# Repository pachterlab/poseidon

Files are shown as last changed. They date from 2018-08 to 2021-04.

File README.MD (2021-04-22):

poseidon_logo



## poseidon: Open source bioinstrumentation
An easy-to-use, highly customizable, and open source syringe pump and microscope system.

**Documentation**: https://pachterlab.github.io/poseidon/

**Paper**: A. Sina Booeshaghi, Eduardo da Veiga Beltrame, Dylan Bannon, Jase Gehring and Lior Pachter, <a href="https://www.nature.com/articles/s41598-019-48815-9">Principles of open source bioinstrumentation applied to the poseidon syringe pump system</a>, Scientific Reports <b>9</b>, Article number: 12385 (2019).

## The tl;dr

The poseidon syringe pump and microscope system is an open source alternative to commercial systems. It costs less than \$400 and can be assembled in an hour. It uses 3D printed parts and common components that can be easily purchased either from Amazon or other retailers. The microscope and pumps can be used together in microfluidics experiments, or independently for other applications. The pumps and microscope can be run from a Windows, Mac, Linux, or Raspberry Pi computer with an easy to use GUI.

ortho_edit

## What is included?
* Computer Aided Design (CAD) files of the 3D printed components.
* Controller software (Python) and a graphical user interface (GUI) to control the pumps.
* Arduino firmware to send commands to the motors and receive commands from the GUI.
* Bill of materials for sourcing and purchasing materials.
* Detailed assembly instructions of hardware components.
* Single click executable files for Mac, Windows, Linux, and Raspberry Pi systems.

<p align="center">
  
</p>

## Getting Started
### 3D printing components and purchasing hardware
The 3D printed components can be fabricated on any desktop fused filament fabrication (FFF) 3D printer. They were designed using [Autodesk Fusion 360](http://autodesk.com/fusion360), a proprietary CAD software that offers free academic licenses.

- Fusion360 interactive view of [poseidon microscope CAD](http://a360.co/2krZoEk).
- Fusion360 interactive view of [poseidon pump](https://a360.co/2Ph19kC).
- STL, STEP, IGES, Fusion 360 archive files, and bill of materials are available in the `HARDWARE/` folder.
- Bill of materials with prices and vendor links on a [Google Spreadsheet](https://docs.google.com/spreadsheets/d/1AHBLf0PbtGDgqNbbK6QO31s7ES9_1uCw_NeKWHHPTM4/edit?usp=sharing).

### Build Videos
Syringe Pump: https://www.youtube.com/watch?v=7YSiO6usR1M  
Microscope  : https://www.youtube.com/watch?v=Szg-vjukonA  
Arduino     : https://www.youtube.com/watch?v=Xl02fsRCJ7U  
Raspberry Pi: https://www.youtube.com/watch?v=g3pXNY8snOg  

Running poseidon: https://youtu.be/VmoB_fPc4L4

### Setting up the Arduino 
We use the [Arduino CNC shield](http://wiki.keyestudio.com/index.php/Ks0095_Arduino_CNC_Kit_/_CNC_Shield_V3.0_%2Bkeyestudio_Uno_R3%2B4pcs_a4988_Driver_/_GRBL_Compatible)
to allow for up to three pumps can be controlled from a computer or from the Rapsberry Pi microscope.

The software is configured to run the stepper motors with 200 steps per revolution at 1/32 microstepping, which translates to 6400 steps per rotation. To configure this, it is necessary to add 3 jumpers between the M0, M1 and M2 pins of the Arduino CNC shield. More information about microstepping can be found in the product page for the [DRV8825 Stepper Motor Driver](https://www.pololu.com/product/2133), which is used by the CNC shield. See the build videos for more detail. 

The Arduino should be flashed with the `arduino_serialCOM_v0.1.ino` sketch, available in the `SOFTWARE/` folder.

**Make sure to download and install the [AccelStepper library](https://www.airspayce.com/mikem/arduino/AccelStepper/index.html)**. To install, unzip the zip file to the libraries sub-folder of your sketchbook, if you get stuck here is a [how-to](https://www.arduino.cc/en/guide/libraries).

The pumps are driven by an Arduino board that interprets commands sent via USB and sends the signals to control the stepper motor movement. For directions on how to flash an arduino please refer to the official guide: https://www.arduino.cc/en/Guide/HomePage

### Installing software
The Python scripts are available in the `SOFTWARE/` folder. The GUI was created using [Qt designer](http://doc.qt.io/qt-5/qtdesigner-manual.html), a drag and drop application for organizing buttons that allows the used to easily make modifications. This GUI is used to interface with a Python script that controls both the microscope and Arduino via USB. 

The software you will need to run on your computer in order to control the Arduino is the `poseidon_main.py` script located in the `SOFTWARE/` folder (also included is `poseidon_controller_gui.py` which is needed). 

You have the option of either (1) running from the source code in Python or (2) choosing the appropriate binary file below for your operating system and executing it. Before you run the controller code, MAKE SURE YOU HAVE INSTALLED THE ARDUINO FIRMWARE!!

## Startup Checklist
Before starting the Python controller, make sure
1. The Arduino has the firmware uploaded to it
2. The Arduino is connected via USB to the computer or Rapsberry Pi microscope
3. You have appropriately placed jumpers on the CNC Sheild to allow for microstepping and hardware enabling (discussed in build video).
4. The CNC shield is powered, and that all motors are plugged in to the CNC sheild

## Running the software and Testing the pumps
There are two ways to run the controller. The easiest way is to just double click the executable available below. Simply download the executable, double click it, and begin using it. Navigate to the **Releases** tab at the top to find the following executables.

- Windows
- Mac OS
- Ubuntu (coming soon)
- Raspbian

# Tips/Hints
Things that we have learned along the way that may help with your build.
- Basic tests indicate that pressures up to 4 MPa can be acheived with 1 microstep and a 1 mL syringe.

- Set the current limit on your motor controller to vary the stall torque. Increasing the current to the motor increases the stall torque and increases the max pressure that your syringe pump can run at. [How to set the current limit](https://www.youtube.com/watch?feature=player_embedded&v=89BHS9hfSUk).

- We recommend [changing the password on the Raspberry Pi](https://raspberrypi.stackexchange.com/questions/67181/how-to-change-a-password) for added security.

- The speeds and flow rates of the system are limited by the microstepping and the syringe size used.

flow_rates

---------------------------------------------------

If you want to run the system from the source code then follow the instructions below.
### Windows, Mac, Linux
First make sure you have Python 3 installed on your machine. Then install PyQt5. To install PyQt5 use `brew install pyqt5` or `conda install pyqt` if you are using anaconda. If you are on Linux you can do `sudo apt-get install python3-pyqt5`. Now we need to add a few packages:
```
pip3 install --upgrade -pip
pip3 install pyserial
pip3 install opencv-python
```
On Linux opencv requires extra binaries
```
sudo apt-get install libatlas-base-dev
sudo apt-get install libjasper-dev
sudo apt-get install libqtgui4
sudo apt-get install libqt4-qt3support
sudo apt-get install libqt4-test
```
Now you can run 
```
# now the script can be called
python3.5 poseidon_main.py
```
### Raspberry Pi
To run `poseidon_main.py` on a Raspberry Pi with a fresh install of Raspbian, Python 3 with pyqt5 need to be installed, together with a few packages.
```
sudo apt-get install python3-pyqt5

# now need to use python3.5 gui.py to invoke the python3 that has pyqt5!
pip3 install --upgrade -pip
pip3 install pyserial
pip3 install opencv-python

# opencv requires a some extra binaries 
sudo apt-get install libatlas-base-dev
sudo apt-get install libjasper-dev
sudo apt-get install libqtgui4
sudo apt-get install libqt4-qt3support
sudo apt-get install libqt4-test

# now the script can be called
python3.5 poseidon_main.py
```
### Now that you have everything installed, go ahead and test it out!
(1) Select the port that your Arduino is plugged into. If you don't see the right port, press `update port`. 
(2) Set your microstepping
(3) Input appropriate settings
(4) Select `connect to controller`
(5) Select `Send all settings to controller`
(6) Go to the controller tab, select all three checkboxes and press `Jog +`

If the sleds are not moving in the right direction simply rotate the relevant stepper motor plug (that connects to the CNC shield) 180 degrees and plug it back in.

## How does it work, and how to modify it. (Very easy!)
The poseidon system was designed to be customizable. It uses the [Raspberry Pi](https://www.raspberrypi.org/)  and [Arduino](https://www.arduino.cc/) electronics boards, which are supported by a strong ecosystem of open source hardware and software, facilitating the implementation of new functionalities.

The pump driver uses an Arduino with a [CNC shield](https://blog.protoneer.co.nz/arduino-cnc-shield/) to run up to three pumps. Each pump has a stepper motor that drives lead screw which in turn moves a sled that is mounted on linear bearings. The displacement of the sled moves the syringe forward or backward allowing the user to dispel or intake liquid.

The controller station uses a Raspberry Pi with a touchscreen to connect to the Arduino and microscope via USB. Because the microscope and Arduino use USB connections, they can alternatively be connected to a computer instead of a Raspberry Pi. 

To modify the 3D models, users can either use Fusion 360 or any other CAD software. Simply open up the components, located in the `HARDWARE` folder, and get editing! Once you're done, go ahead and print out the parts and assemble them.

Most of the modifications to the code will be done in `poseidon_main.py` and to the GUI. If you want to edit the GUI, first make sure you have installed PyQt Designer (which should have been installed when you downloaded and installed PyQt5, so you can search for it on your computer `Designer.exe` (Windows) or `Designer` in your applications folder (Mac). Open up the `poseidon_controller_gui.ui` in Designer and make whatever modifications you'd like. Then when you are done, you need to convert the modified `.ui` file to a `.py` file. Go to the terminal, navigate to the folder where you have `poseidon_controller_gui.ui` and run the command `pyuic5 poseidon_controller_gui.ui > poseidon_controller_gui.py`.

When you are done editing the `poseidon_main.py` you can recreate the single click executable files by following the instructions below.

### Installing pyinstaller on Windows 7 and making a single executable for the Python controller
 
Using Python 3.7 (installing pyqt5 form pip) or 3.4 (installing pyqt5 from executable) on Windows 10 did not work. 
Python 3.7 yields terrible dependency errors from pyinstaller and with Python 3.4 after making the executable pyqt complains apparently because of windows 10. The solution was to use a machine with Windows 7. 

After installing Python 3.5.4 (https://www.python.org/downloads/release/python-354/), using the `Windows x86-64 executable installer`, these dependencies should install without problems:
```
python -m pip install pyqt5
python -m pip install pyserial
python -m pip install opencv-python
```
To compile a binary you should write `PyInstaller`, instead of `pyinstaller`...
```
python -m PyInstaller --version
python -m PyInstaller poseidon_main.py
```
Just doing `python -m PyInstaller gui.py` with Python 3.5 on windows 7 threw up some errors, the following line solved the issue.
Described here: https://stackoverflow.com/questions/51324754/python-3-6-x-pyinstaller-gives-error-no-module-named-pyqt5-sip
```
python -m PyInstaller -F poseidon_main.py --hidden-import PyQt5.sip
```
## Safety Considerations
Please review the license before using/developing/distribution poseidon. 

The poseidon syringe pump system uses 3D printed PLA plastic and standard off the shelf components which do not pose a health hazard if handled correctly. Improper handling of plastics however can create hazards when working with organic solvents. Initial tests of the poseidon syringe pump showed excessive bending of the syringe pump body. We mitigated this by reinforcing the body with set screws and a thicker base. To mitigate the possibility of catastrophic failure due to clogging we set the reference voltage on the motor controller such that the motor stalls when the pressure in a 1 mL syringe reaches 4 MPa.

Before using the poseidon system in a wetlab environment, please ensure that you have thoroughly tested its functionality for your use case in a dry lab. Once the poseidon system has been moved into a wetlab, it should not be moved back to a drylab or dry workbench.

If you plan to build on the poseidon system, ensure that you communicate any safety concerns that you may have with your design to potential users and collaborators.

## Authors

The poseidon system was developed by the [Pachter Lab](https://pachterlab.github.io) at Caltech by:
- [Sina Booeshaghi](https://sinabooeshaghi.com/)
- [Eduardo Beltrame](https://github.com/munfred/)
- [Dylan Bannon](https://github.com/dylanbannon/)
- [Jase Gehring](https://scholar.google.com/citations?user=63ZRebIAAAAJ&hl=en)
- [Lior Pachter](https://github.com/lakigigar)

#### Prior work and references

The poseidon project is based on a number of other open source projects and papers.

The pump design was based on the open source syringe pumps published by the [Pearce Research Group](http://www.mse.mtu.edu/~pearce/Index.html):

[Open-Source Syringe Pump Library <br>
Bas Wijnen, Emily J. Hunt, Gerald C. Anzalone, Joshua M. Pearce <br>
PLOS One, 2014. https://doi.org/10.1371/journal.pone.0107216](http://journals.plos.org/plosone/article?id=10.1371/journal.pone.0107216)

With subsequent refinements published on [http://www.appropedia.org/Open-source_syringe_pump](http://www.appropedia.org/Open-source_syringe_pump)

The microscope was based on a design published by the [Satija Lab](http://satijalab.org/):

[Single-Cell Single-cell RNA-seq of rheumatoid arthritis synovial tissue using low-cost microfluidic instrumentation <br>
William Stephenson, Laura T. Donlin, Andrew Butler, Cristina Rozo, Ali Rashidfarrokhi, Susan M. Goodman, Lionel B. Ivashkiv, Vivian P. Bykerk, Dana E. Orange, Robert B. Darnell, Harold P. Swerdlow, Rahul Satija <br>
Nature Communicationsvolume 9, Article number: 791 (2018)](https://www.nature.com/articles/s41467-017-02659-x)

All necessary files are available on [Metafluidics](https://metafluidics.org/devices/minidrops/)

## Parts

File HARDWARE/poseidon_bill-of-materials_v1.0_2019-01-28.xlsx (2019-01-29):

Poseidon Pumps
Total for 3 pumps | $174.87 |  |  |  | Per pump total | 37.90810303
Part Number | Item Description | Package Cost | Packages for 3 pumps | Items per pump | Cost for 3 pumps | Cost per pump | Cost for single pump | Retailer | Items per pack | Price per item | Link
1 | Nema 17 Stepper Motor (Bipolar, 40mm, 45Ncm) | 33.99 | 1 | 1 | 33.99 | 11.33 | 33.99 | Amazon | 3 | 11.33 | https://www.amazon.com/Stepper-Holding-Printer-Beauty-Star/dp/B075S98D46
2 | 5mm to 5mm Motor Shaft Coupling | 22 | 1 | 1 | 22 | 2.2 | 22 | Amazon | 10 | 2.2 | https://www.amazon.com/Aluminum-Flexible-Coupling-Printing-Pack/dp/B01EFFBM4I?s=industrial
3 | 6mm Steel Rod (length 200mm, pack of 2) | 7.12 | 3 | 2 | 21.36 | 7.12 | 7.12 | Amazon | 2 | 3.56 | https://www.amazon.com/Steel-Round-Turning-Lathe-200mm/dp/B00LUSVKVY
4 | 6mm Linear Bearing (pack of 12) | 12.49 | 1 | 2 | 12.49 | 2.081666667 | 12.49 | Amazon | 12 | 1.040833333 | https://www.amazon.com/uxcell-6mmx12mmx19mm-Linear-Bushing-Bearing/dp/B01MTLSZFQ?s=industrial
5 | M5x0.8 Threaded Rod (length 170mm) | 9.14 | 1 | 1 | 9.14 | 1.828 | 9.14 | Amazon | 5 | 1.828 | https://www.amazon.com/uxcell-170mm-Stainless-Threaded-Fasteners/dp/B01M4L8JDC?s=industrial
6 | M5x0.8 nut | 7.2 | 1 | 1 | 7.2 | 0.144 | 7.2 | Amazon | 50 | 0.144 | https://www.amazon.com/uxcell-Metric-M5x0-8mm-Stainless-Finished/dp/B012T3C8YQ?s=industrial
7 | M3x0.5 socket head screws to mount motor (length 20mm) | 9.91 | 1 | 4 | 9.91 | 0.3964 | 9.91 | Amazon | 100 | 0.0991 | https://www.amazon.com/Stainless-Socket-Internal-Threaded-Threads/dp/B000FN21AO?s=industrial
8 | M3x0.5 socket head screws (hold rod in place, length 10mm) | 7.8 | 1 | 2 | 7.8 | 0.2836363636 | 7.8 | Amazon | 55 | 0.1418181818 | https://www.amazon.com/uxcell-M3x10mm-Thread-Stainless-Socket/dp/B01MFA9YEP?s=industrial
9 | M3 nut (hold rod in place) | 5.2 | 1 | 2 | 5.2 | 0.104 | 5.2 | Amazon | 100 | 0.052 | https://www.amazon.com/100Pcs-Female-Thread-Fastener-Silver/dp/B00GYS1SXU?s=industrial
10 | M5 knob (hold syringe in place) | 11.9 | 1 | 1 | 11.9 | 1.19 | 11.9 | Amazon | 10 | 1.19 | https://www.amazon.com/Kipp-06220-405X50-Thermoplastic-External-Diameter/dp/B013I72QTY?s=industrial
11 | 12V power unit (end stripped to fit CNC shield power input) | 15 | 1 | 1 | 15 | 5 | 5 | Amazon | 1 | 15 | https://www.amazon.com/Kastar-AC-Adapter-Power-LCD/dp/B003TUMDWG?s=electronics
12 | Arduino + CNC Shield Pack | 18.88 | 1 | 0.33 | 18.88 | 6.2304 | 18.88 | Amazon | 1 | 18.88 | https://www.amazon.com/Longruner-Expansion-Stepper-Heatsink-Arduino/dp/B06XJKVLG3
Poseidon Microscope
Total microscope | $180.37
Part Number | Item Description | Package Cost | Packages needed | Items needed | Cost | Items per pack | Retailer | Link
1 | Raspberry Pi Motherboard | 35.75 | 1 | 1 | 35.75 | 1 | Amazon | https://www.amazon.com/Raspberry-Pi-RASPBERRYPI3-MODB-1GB-Model-Motherboard/dp/B01CD5VC92?s=pc
2 | Raspberry Pi 7" touchscreen display | 69.99 | 1 | 1 | 69.99 | 1 | Amazon | https://www.amazon.com/Raspberry-Pi-7-Touchscreen-Display/dp/B0153R2A9I
3 | Raspberry Pi Power Suppy (5v 1.5A DC) | 9.99 | 1 | 1 | 9.99 | 1 | Amazon | https://www.amazon.com/CanaKit-Raspberry-Supply-Adapter-Charger/dp/B00MARDJZ4?s=electronics
4 | 16gb MicroSD card (comes with adapter) | 6.95 | 1 | 1 | 6.95 | 1 | Amazon | https://www.amazon.com/SanDisk-16GB-Micro-SDHC-Memory/dp/B004G605OA?s=electronics
5 | USB Microscope | 20.99 | 1 | 1 | 20.99 | 1 | Amazon | https://www.amazon.com/Jiusion-Magnification-Endoscope-Microscope-Compatible/dp/B06WD843ZM/
6 | Keyboard + Mouse Bundle (wired) | 13.09 | 1 | 1 | 13.09 | 1 | Amazon | https://www.amazon.com/AmazonBasics-Wired-Keyboard-Mouse-Bundle/dp/B00B7GV802?s=electronics
7 | M3x0.5 Socket Head Screws (length 10mm) | 7.8 | 1 | 4 | 7.8 | 55 | Amazon | https://www.amazon.com/uxcell-M3x10mm-Thread-Stainless-Socket/dp/B01MFA9YEP?s=industrial
8 | M5x0.8 Socket Head Screw (length 14mm) | 8.61 | 1 | 8 | 8.61 | 15 | Amazon | https://www.amazon.com/uxcell-M5x14mm-Stainless-Metric-Thread/dp/B01LJROXK0
9 | M5x0.8 nuts | 7.2 | 1 | 8 | 7.2 | 50 | Amazon | https://www.amazon.com/uxcell-Metric-M5x0-8mm-Stainless-Finished/dp/B012T3C8YQ?s=industrial

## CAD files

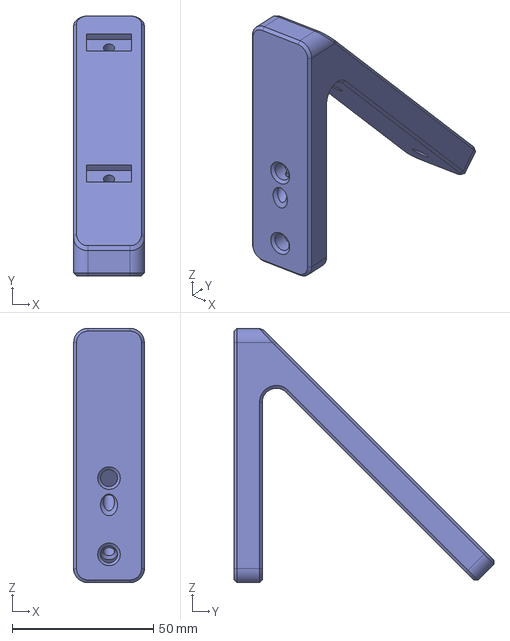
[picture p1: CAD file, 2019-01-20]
HARDWARE/microscope/step/Scope Screen Leg Mount.step
25.0 x 92.0 x 90.0 mm

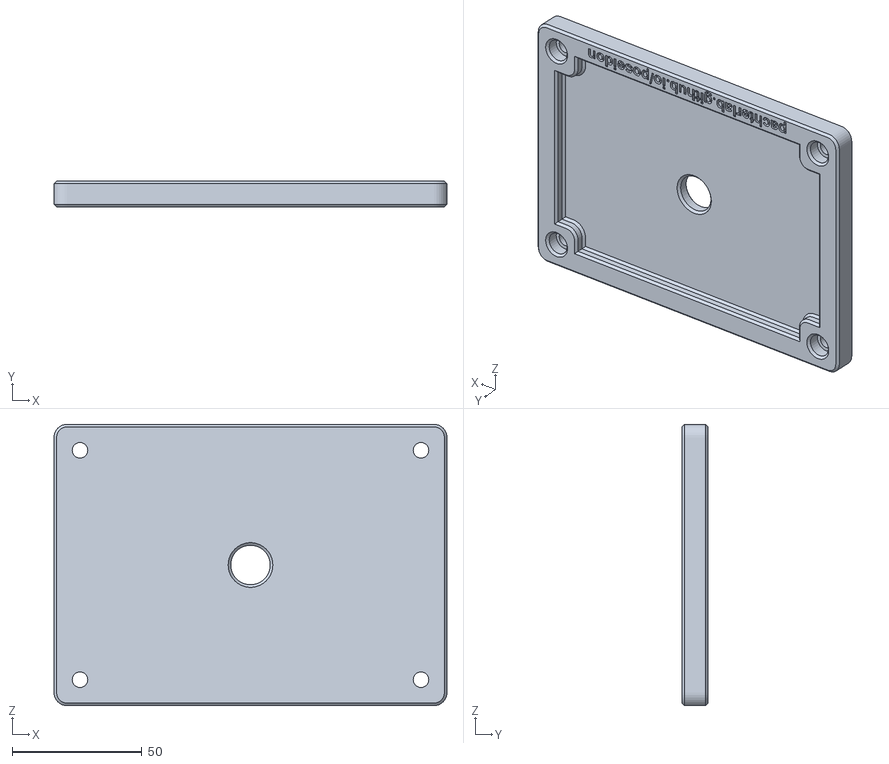
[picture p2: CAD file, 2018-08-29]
HARDWARE/microscope/stl/Scope Top Stage v33.stl
151.2 x 10.0 x 108.3

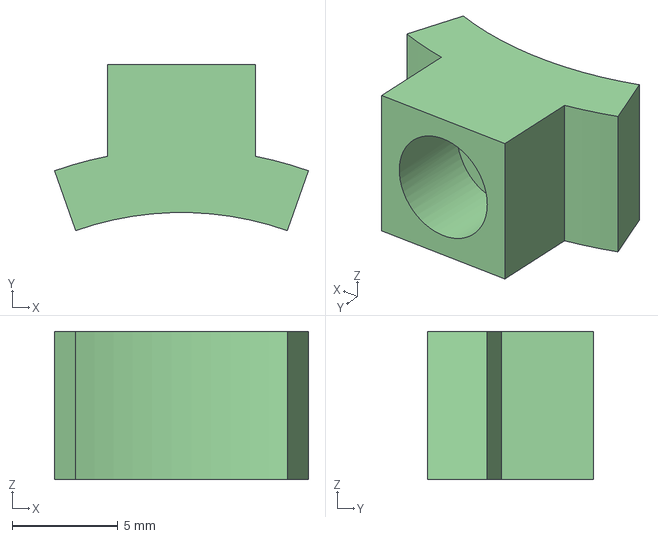
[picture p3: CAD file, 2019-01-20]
HARDWARE/pump/step/Pump Syringe Brace.step
12.0 x 7.86 x 7.00 mm

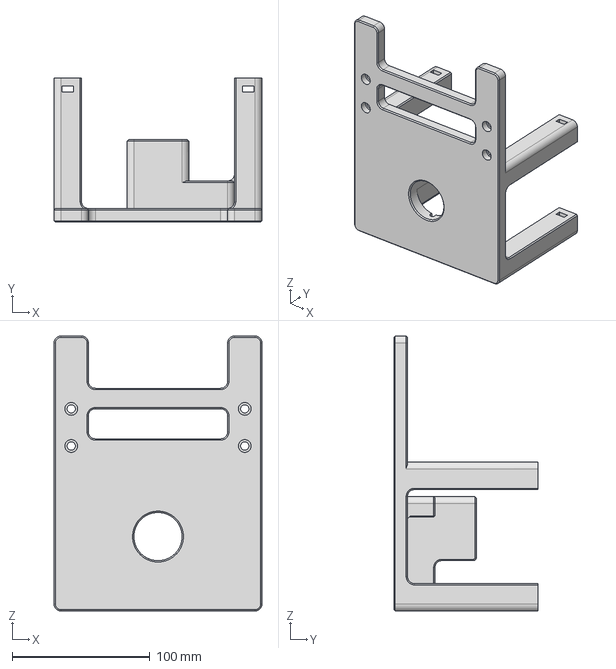
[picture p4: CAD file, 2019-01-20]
HARDWARE/microscope/step/Scope Base.step
151.2 x 105.0 x 200.0 mm

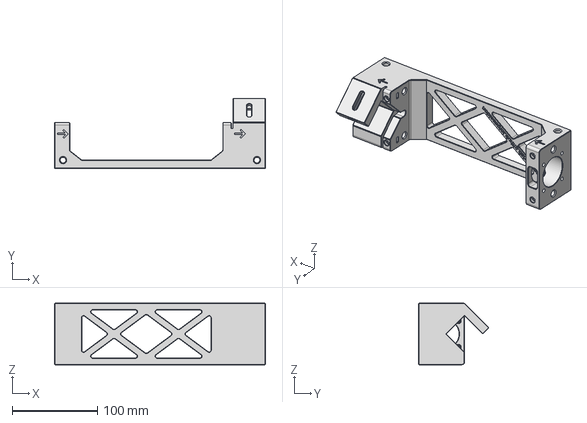
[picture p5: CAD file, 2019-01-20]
HARDWARE/pump/step/Pump Base.step
247.0 x 82.3 x 72.0 mm

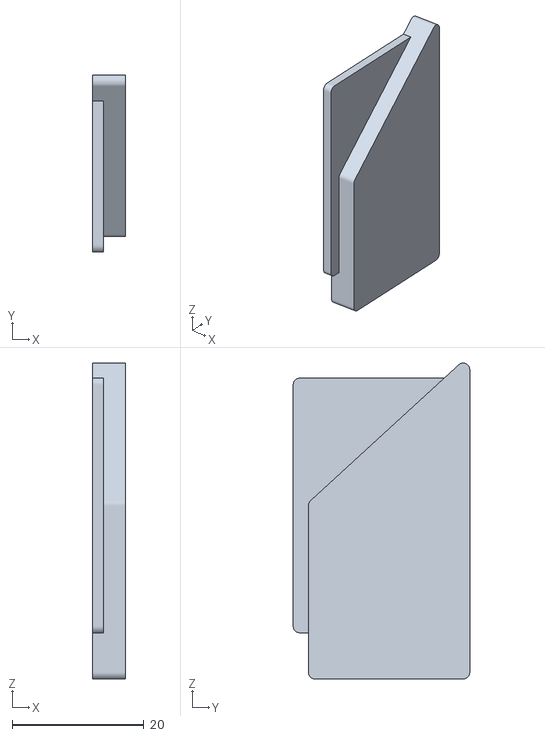
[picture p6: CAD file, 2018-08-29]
HARDWARE/pump/stl/Pump Cover Slide v51.stl
5.00 x 26.8 x 47.9

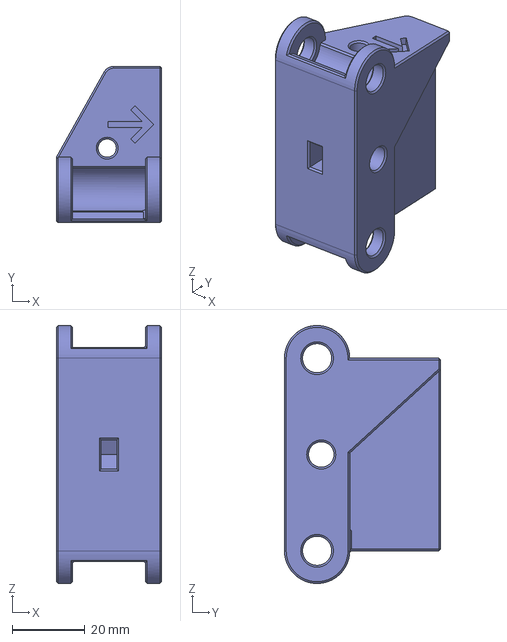
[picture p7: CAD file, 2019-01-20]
HARDWARE/pump/step/Pump Carriage.step
29.0 x 43.0 x 71.0 mm

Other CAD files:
HARDWARE/pump/stl/Pump Syringe Brace v51.stl
HARDWARE/microscope/stl/Scope Base v33.stl
HARDWARE/microscope/step/Scope Top Stage.step
HARDWARE/microscope/stl/Scope Screen Leg Mount v33.stl
HARDWARE/pump/stl/Pump Base v51.stl
HARDWARE/pump/step/Pump Cover Slide.step
HARDWARE/pump/stl/Pump Carriage Sled v51.stl
HARDWARE/microscope/iges/Scope Base.iges
HARDWARE/microscope/iges/Scope Screen Leg Mount.iges
HARDWARE/microscope/iges/Scope Top Stage.iges
HARDWARE/pump/iges/Pump Base.iges
HARDWARE/pump/iges/Pump Carriage.iges
HARDWARE/pump/iges/Pump Cover Slide.iges
HARDWARE/pump/iges/Pump Syringe Brace.iges

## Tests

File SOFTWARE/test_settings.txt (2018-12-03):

File name: /Users/sinabooeshaghi/Dropbox (Personal)/Caltech/Research/Syringe Pump/poseidon/SOFTWARE/test_settings.txt
Date time: 2018-12-03 15_39_08
:================================ 
P1 Syrin: BD 1 mL
P1 Units: mm/s
P1 Speed: 1.0
P1 Accel: 5.0
P1 Jog D: 1.0
:================================ 
P2 Syrin: BD 1 mL
P2 Units: mm/s
P2 Speed: 1.0
P2 Accel: 5.0
P2 Jog D: 1.0
:================================ 
P3 Syrin: BD 1 mL
P3 Units: mm/s
P3 Speed: 1.0
P3 Accel: 5.0
P3 Jog D: 1.0
Exp Note:

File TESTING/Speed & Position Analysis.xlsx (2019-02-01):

1/32 Microstep | Number of Pumps Running | Set speed (mm/s) | Set Travel distance (mm) | Inferred Set Time (s) | Measured time (s) | Measured Distance (mm) | Measured Speed (mm/s) | Distance Error (mm, signed) | Distance Percent Error | Speed Error (mm/s, signed) | Percent Speed Error
1 | 1 | 0.01 | 0.1 | 10 | 10.64 | 0.1 | 0.009398496241 | 0 | 0 | -0.0006015037594 | 6.015037594
2 | 1 | 0.01 | 0.1 | 10 | 10.73 | 0.1 | 0.009319664492 | 0 | 0 | -0.0006803355079 | 6.803355079
3 | 1 | 0.01 | 0.1 | 10 | 10.54 | 0.1 | 0.009487666034 | 0 | 0 | -0.0005123339658 | 5.123339658
4 | 1 | 0.01 | 0.1 | 10 | 10.53 | 0.1 | 0.009496676163 | 0 | 0 | -0.0005033238367 | 5.033238367
5 | 1 | 0.01 | 0.1 | 10 | 10.57 | 0.1 | 0.009460737938 | 0 | 0 | -0.0005392620624 | 5.392620624
6 | 1 | 0.01 | 0.1 | 10 | 10.51 | 0.1 | 0.009514747859 | 0 | 0 | -0.0004852521408 | 4.852521408
7 | 1 | 0.01 | 0.1 | 10 | 10.54 | 0.1 | 0.009487666034 | 0 | 0 | -0.0005123339658 | 5.123339658
8 | 1 | 0.01 | 0.1 | 10 | 10.52 | 0.1 | 0.009505703422 | 0 | 0 | -0.0004942965779 | 4.942965779
9 | 1 | 0.01 | 0.1 | 10 | 10.51 | 0.11 | 0.01046622265 | -0.01 | 10 | 0.0004662226451 | 4.662226451
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

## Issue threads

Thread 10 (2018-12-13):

pachterlab/poseidon #10: Steppers are not independant !

Xqua, 2018-12-13:
Steps:

1) Set settings on the settings tab, example 
1: 0.1mm/s
2: 1mm/s
3: 10mm/s

2) Click send all settings

3) Go to syringe control

4) Click run 

The 3 steppers go at the same rotation speed !

Also, the numbers do not update on the Syringe control tab

sbooeshaghi, 2018-12-13:
Hey Xqua,

A couple of things, if you have your microstepping jumpers placed on your CNC sheild board, you need to specify the microstepping amount (1/32, 1/16 etc) in the python code under the unit conversion functions (we have not automated this yet). Also the range of speeds for the carriage is limited by the microstepping that you select. For example if you select 1/32 microstepping you wont be able to go 5mm/s. We don't have exact speed ranges yet for the different microsteps but we are working on it. Also make sure also that you are using stepper motors with 200 steps as that will affect the speed.

Second there is a known bug that we are working on fixing and that is the following: the very first time you press "Run" or "Jog +/Jog-" after you send your settings, then the speed of the motors is not accurate. A temporary workaround is to send your settings, then press "Jog +", then immediately press stop. Now if you press "Jog" or "Run" the steppers should run at the appropriate speed. Keep in mind you will have to do this after every speed change. (yes this is annoying and yes we will fix it :) )

Lastly, we have set the acceleration for the motors to a fixed value in the arduino code in this release as we were having some issues with varying the acceleration from the GUI.

I hope that helps! Please let me know if there are any other problems that arise.

Sina B.

Xqua, 2018-12-13:
Hi ! 

Yes this already helps (I think ?)
Alright, so I followed the poseidon tutorial, a bought the steppers you recommended (so there should not be any discrepancy here)

So for example I set this
[image]

Then went here, clicked Jog + then Stop
Then set as below

[image]

What I am expecting is for pump 3 to run 1 second, pump 2 for 2 sec, and pump 1 for 10 sec right ? 
(1 mm each with different speed)

But the 3 will run for about 30 seconds 

And at about the same speed (visually ... )

Xqua, 2018-12-13:
(Also I have experience with python and arduino so I'll be happy to help with those bugs ^^ but I was just trying an "out of the box" trial)
Also were in the code is this unit conversion 1/32 ?

this line ? `mm = steps/200/32*0.8` 
Because it's already set ! :D

Xqua, 2018-12-13:
also I believe this is probably a typo ?
[image]

Where this should be 

      stepper1.move(p1_distance_left);
      stepper2.move(p2_distance_left);
      stepper3.move(p3_distance_left);
      while (stepper1.distanceToGo() >= 0 && stepper2.distanceToGo() >= 0 && stepper3.distanceToGo() >= 0) {

sbooeshaghi, 2018-12-14:
Thanks for the info that helps out! Can you do the following for me, can you comment out `line 1104` and uncomment `line 1105`, and comment out `line 1118` and uncomment 1119 in poseidon_main.py using  the hashtag "#"?

You then have two options to run the software, you can recompile the executable or you can go to your terminal and run `python3 poseidon_main.py`

Then try running your settings again and let me know if that works!

Sina B.

sbooeshaghi, 2018-12-14:
> also I believe this is probably a typo ?
> [image]
> 
> Where this should be
> 
> ```
>   stepper1.move(p1_distance_left);
>   stepper2.move(p2_distance_left);
>   stepper3.move(p3_distance_left);
>   while (stepper1.distanceToGo() >= 0 && stepper2.distanceToGo() >= 0 && stepper3.distanceToGo() >= 0) {
> ```

Yes there is! I'll fix it. Thank you :)

Xqua, 2018-12-14:
Ahahah yes ! this 32 divisions was the trick !

Xqua, 2018-12-14:
All good now, you should prob change this in the github code ;)

closed 2018-12-14 by Xqua

sbooeshaghi, 2018-12-14:
Great! Glad it worked out. I appreciate you trying it "out of the box" it helps identify these bugs :)

I'll go ahead and make those changes now.

Sina B.

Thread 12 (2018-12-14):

pachterlab/poseidon #12: GUI number not updating

Xqua, 2018-12-14:
Alright so moving on to the next bug I guess. 

[image]

This part of the GUI is not updating ? Whatever one does, it either stays to 0 or display some cryptic (.59??) number for pump 1 only

sbooeshaghi, 2018-12-14:
This feature has not been successfully implemented yet, maybe I should remove it from the GUI so as to not confuse users.

I was having an issue with the amount of Serial Prints I was sending from the Arduino to display these positions so I left it at that..

Sina B.

Xqua, 2018-12-14:
Hum ... 
Could you not do an estimate ? 
As the arduino is going to run until a new command is sent, it should take milliseconds for the command to go through. 
Therfore you can either measure it, or just assume t = 0 and then run an estimate based on the speed of the motor ? 

And send from the arduino the current position every ... 10 / 100 loop ? just to adjust ?

sbooeshaghi, 2018-12-17:
Hmm not a bad idea! I'll play around with it and see what sort of results I get. Thank you again for the suggestions!

Sina B.

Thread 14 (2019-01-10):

pachterlab/poseidon #14: Recoding the arduino code

Xqua, 2019-01-10:
Hi, 

I'm cleaning the code of the arduino code. 
It's really hard to debug because of the very high number of switch case statements ! 
So I'm putting it all in loops. 
For example, runfew() becomes

```

void runFew() {
  // First we determine the direction of movement. If 1, then it's forward, otherwise it's -1.
  // We use 1 and -1 so that we can multiply any number and reverse the math, minimizing lines of code 
  int direction = 1;
  if (strcmp(dir, "B") == 0) {
    direction = -1;
  }
  // Second we set the distance to move for each stepper.
  // We use direction and multiply the value saved in the distances array;
  // The distances array is set above to default to 999999 if 'RUN' else, the value set.  
  for (int i = 0; i < 3; i += 1) {
    if (motors[i] == 1) {
      toMove = direction * distances[i];
      steppers[i].move(toMove);
    }
  }
  // Finally the main loop where we move and check the steppers status
  // We declare an array to store the status of each stepper  
  int stepperStatus[3] = [0, 0, 0];
  // Then we loop until that sum is equal to the number of selected steppers
  // That number is stored in the motors array, 1 for selected, 0 otherwise
  // If we have 1 and 3 for example motors = [1, 0, 1] => sum = 2 
  while (array_sum(stepperStatus) != array_sum(motors)) {
    // We iterate over the 3 possible steppers
    for (int i = 0; i < 3; i += 1) {
      // If this stepper is selected
      if (motors[i] == 1) {
        // Ask the stepper to move to position at constant speed. 
        steppers[i].runSpeedToPosition();
        // Check if it reached it's position
        if ((direction * steppers[i].distanceToGo()) => 0) {
          // If yes then store that value in the stepperStatus array.
          stepperStatus[i] = 1;
        }
      }
    }
    getDataFromPC();
  }
  clearVariables();
}
```

I have a few questions though! 
Why do you use the `runSpeedToPosition()` instead of the `run()` function ? 
It will work just fine, but will not allow for the use of the acceleration parameter as per the documentation (https://www.airspayce.com/mikem/arduino/AccelStepper/classAccelStepper.html#a9270d20336e76ac1fd5bcd5b9c34f301) 

I don't think for microfluidics application that the acceleration matters?

Anyhow I'll be doing a series of PR soon.

sbooeshaghi, 2019-01-10:
Clever solution! This was my first time coding in Arduino and my first 'naive' solution was switch cases. 

Also apologies for getting back to you so late, I was on vacation and school just started back up. This looks good! I am now available and will review the PR's as they come in.

To answer your questions: I was using `runSpeedToPosition()` in the testing phase since I was first and foremost concerned with testing constant speed flow rates. I do think the `run()` function should be used with an acceleration parameter as you suggested for the following reason:

The use case when using acceleration would be to do whats called "gradient flow" pumping, where the acceleration is set as constant such that the flow rate increases from 0 to a maximum value over the course of an experiment.

Xqua, 2019-01-10:
Awesome ! 

I'm finished the first pass of cleaning. Now I'm testing the new code. I'll let you know as soon as it's functional ;)

Xqua, 2019-01-10:
Also, why do you run the servos at 1/32 microstepping ? It's veryyyy fine grain ! Any reason ?

sbooeshaghi, 2019-01-11:
Great question! So I opted for 1/32 microstepping to get flow rates ~900 µL/hr using a 3mL syringe. This is necessary for the types of biological experiments we are doing in the lab (droplet based microfluidics). 

Take a look at this paper https://www.nature.com/articles/nprot.2016.154#f1. We pump oil and water (with a few other chemicals) to create hydrogel beads! These beads are then used in a single-cell RNA sequencing experiment, here's a good paper describing the application (which may not be good depending on your background): https://www.ncbi.nlm.nih.gov/pmc/articles/PMC5900446/

I am currently in the process of characterizing the "accessible" flow rates for each microstepping setting to see what flow rates an experimenter can achieve with the different microsteps. For example, if I set my microstepping to 1/32, can I get carriage speeds of 10mm/s? First pass experiments say no, and as such I would like to find what is the maximum carriage speed achievable under 1/32 microstepping, and under 1/16, and under 1/8 etc..

I have used 1/32 microstepping in the pumps to make hydrogel beads, using microfluidics, and have successfully synthesized the beads (of the appropriate size) as described in the paper above. So I know that 1/32 works for pumping at ~900µL/hr flow rates! The goal now is to be more concrete about microstep setting and achievable flow rate, and thats what these next basic tests that I am running, are for.

Munfred, 2019-01-11:
> I know of thoose beads ;) I'm building this rig for doing inDrop ^^

Oh nice! We're also setting up inDrops. Which lab do you work at?

Xqua, 2019-01-11:
Extavour Lab at Harvard

sbooeshaghi, 2019-01-13:
Thank you again @Xqua for the suggestions! I went ahead and merged your PR. I also made a few updates to the code which allow for changing the microstepping value in the GUI (but an associated hardware change is still needed.)

Im going to close out this issue since I think everything is resolved. Please let me know if you come across anything else!

closed 2019-01-13 by sbooeshaghi

Xqua, 2019-01-13:
Sounds good ! I'll let you know if I see other bugs as I'm.using this or if I do other enhancements.

Closed #14.

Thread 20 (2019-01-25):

### ISSUE TITLE
Low flow rate error

### ISSUE THREAD

**Issue by Munfred** [pachterlab/poseidon#20]
There is a known bug that we are working on fixing and that is the following: the very first time you press "Run" or "Jog +/Jog-" after you send your settings, then the speed of the motors is not accurate. A temporary workaround is to send your settings, then press "Jog +", then immediately press stop. Now if you press "Jog" or "Run" the steppers should run at the appropriate speed. Keep in mind you will have to do this after every speed change. :(

**Comment by sbooeshaghi** [comment]
This was fixed in commit 9c36cc5 made for the `arduino_serialCOM_v0.1.ino` file.

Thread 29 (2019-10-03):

pachterlab/poseidon #29: Size of the pump for 3D printing & standard 3D printer bed size

jcmolloy, 2019-10-03:
I am printing off the component parts but I only have access to a printers with a build base of 22 cm (Ultimaker, Prusa i3, Ender 3). The STL is 25 cm - any suggestions other than finding someone with a bigger printer? 

I looked at the model vertically as it will fit into the Ultimaker Extended but seems like a brutal overhang! It would be great if you could confirm your printing strategy before I try and end up with a mess. Thanks very much!

sbooeshaghi, 2019-10-03:
We have not tried printing the pump vertical with that overhand, but I don't see why it shouldn't work! All of our pumps have been printed on a Makergear M2.

You may know this but there are services that offer to print parts for quite cheap. This may be something to look in to.

Sina B.

closed 2019-10-03 by sbooeshaghi

jcmolloy, 2019-10-04:
Thanks @sbooeshaghi. I figured as I have access to eight types of 3D printer and a lot of filament I should be able to make it work without outsourcing 🙂. Ultimaker recommend a max 1-2mm unsupported 90 degree overhangs so if you haven't successfully tried then I don't think it's likely to work. I'll redesign the Fusion360 model to fit a 22cm bed and I'll report back and share the file if it all works out.

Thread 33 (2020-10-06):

pachterlab/poseidon #33: The commands were not sent to stepper motors; however, the board connected to the gui controller successfully

maydanshahi, 2020-10-06:
I have followed all structures but The commands were not sent to stepper motors; however, the board connected to the gui controller successfully. I validated the arduino uno, cnc shield and stepper motors with another firmware (grbl) and every thing was okay. The commands sent to the board and then stepper motors successfully but when I use the poseidon structures, I faced to this problem. The controller was connected to board successfully, and the commands were sent to the arduino board correctly, but the stepper motors were not work. What should I do? could anyone help me?

gallagherk17, 2021-04-12:
Hey did you ever figure this out? I am facing a similar issue.

maydanshahi, 2021-04-27:
Hi
Not yet

Mubeen5611, 2023-03-18:
Is you resolve that issue then plz guide me

Mubeen5611, 2023-03-18:
Command was not sent to motor plz guide

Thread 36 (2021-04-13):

### ISSUE TITLE
Settings never finish sending

### ISSUE THREAD

**Issue by gallagherk17** [pachterlab/poseidon#36]
I have flashed the arduino and have the gui working and it says it sends commands, however the motor does not respond to the commands.  Not sure what is going on or what the issue is.

**Comment by sbooeshaghi** [comment]
Hi @gallagherk17 can you please close this issue and make a new one following the Bug report template? This will help us better diagnose what exactly is going one. 

If you click on "New Issue" then click on "Get Started" you'll see the issue template; I just made that option available. Once you do, please close this issue.

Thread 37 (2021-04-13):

pachterlab/poseidon #37: Commands are not reflected in motor movement

gallagherk17, 2021-04-13:
**Describe the bug**
A clear and concise description of what the bug is.
I have connected to the controller and have sent the settings but when I try to jog or run the motor nothing happens.  The code seems to be sending to the Arduino but nothing is occurring as the output

**To Reproduce**
Steps to reproduce the behavior:
1) Set settings to:
[image]
2) Try to Jog + (10mm)
3) No response from motor

No error is populated in code
[image]

**Expected behavior**
A clear and concise description of what you expected to happen.
I would expect the motor would jog forward about 10mm 

**Screenshots**
If applicable, add screenshots to help explain your problem.
My Arduino set up
[image]

**Software versions (please complete the following information):**
 - OS: Windows
- Python version 3.6

**Additional context**
I am new to arduinos but I have been trying to follow all the steps you have laid out.  Any help on how to solve this issue would be greatly appreciated.

sbooeshaghi, 2021-04-15:
Have you placed jumpers underneath the motor controller (in the CNC shield) to correspond to 32 microstepping?

Mubeen5611, 2023-03-18:
> Have you placed jumpers underneath the motor controller (in the CNC shield) to correspond to 32 microstepping?

Is you resolve that issue plz guide me

Mubeen5611, 2023-03-18:
> **Describe the bug** A clear and concise description of what the bug is. I have connected to the controller and have sent the settings but when I try to jog or run the motor nothing happens. The [...]

Is you resolve that problem

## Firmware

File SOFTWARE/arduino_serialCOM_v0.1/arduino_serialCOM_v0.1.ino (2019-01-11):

//#include <lc.h>
//#include <lc-addrlabels.h>
//#include <pt-sem.h>
//#include <lc-switch.h>
//#include <pt.h>

// TODO:
// (1) Figure out how to report distance remaining back to python
// (2) Combine the run and jog functions into a move function
// (3) Then also combine one, few, and all movements into 1 function
// (4) Figure out how to enable/disable steppers without using the jumper that way we can control the enabling via gui

// NOTES:
// (1) All values are reported to the arduino in steps (not mm or any other units!)
// (2) With 32 microstepping, and a 200 step motor, there are effectively 6400 steps per rev
// (3) The reporting the distance left will reutnr "steps remaining"

// WRITE COMMAND: <RUN,DIST,123,F,0.0,0.0,0.0>

// ======================================================
// ACCELSTEPPER FUNCTIONS: returns fncName(argtype arg) [description]
// ======================================================

// SETTINGS
// --------
// void setMaxSpeed(float speed>0)            [run() will accelerate to speed in steps per sec]
// void setAcceleration(float acceleration>0) [sets the accel in steps per sec per sec]
// void setSpeed(float speed)                 [runSpeed() will use this amount. >0 is clockwise, <0 counterclockwise]

// #########I DON'T USE THESE###########
// void setMinPulseWidth(unsignedint minWidth)
// void setEnablePin(uint8_t enablePin=0xff)
// void setPinsInverted(bool directionInvert=false, bool stepInvert=false, bool enableInvert=false)
// void setPinsInverted (bool pin1Invert, bool pin2Invert, bool pin3Invert, bool pin4Invert, bool enableInvert)
// #########I DON'T USE THESE###########

// SET MOVEMENT
// ------------
// void moveTo(long absolute)
// void move(long relative)
// void setCurrentPosition(long position)      [resets the current position of the motor to ZERO. this is the ZERO!! side effect: sets speed=0]

// RUN
// -----------
// void runToPosition()                        [BLOCKING; moves with accel and decell to target (runToNewPosition()) calls this fnc, then this calls run()]
// void runToNewPosition(long position)        [BLOCKING; moves with accel and deccel to target position (absolute position) moves with run()]
// bool run()                                  [move motor one step if a step is due. this implements accel and decell. uses setMaxSpeed]
// bool runSpeed()                             [move motor one step if a step is due. does not implement accel and decell (ie inf accel). uses setSpeed()]
// bool runSpeedToPosition()                   [runs at currently selected speed until target position is reached, does not use accel]
// void stop()                                 [changes target pos s.t. stepper stops as quickly as possible. uses accel and decell]
// void disableOutputs()
// void enableOutputs()

// I am confused how the calls work for these functions. need to review

// GETTERS
// ------------
// long distanceToGo()                         [returns distance in steps from targetPosition. >0 is clockwise from current pos, <0 ccw]
// long targetPosition()                       [the most recently set target pos, >0 is cw from the ZERO and <0 is ccw from current]
// long currentPosition()                      [current motor position >0 cw from the ZERO position
// bool isRunning()
// float maxSpeed()
// float speed()

// =============================== Code starts here ================================================================

#include <AccelStepper.h>

// First we create the constants that we will use throughout our code
#define MOTOR_STEPS 200
#define MICROSTEPS 32
#define TOTAL_STEPS 6400

#define X_SPEED 1000 // X steps per second
#define Y_SPEED 1000 // Y
#define Z_SPEED 1000 // Z

#define X_ACCEL 5000.0 // X steps per second per second
#define Y_ACCEL 5000.0 // Y
#define Z_ACCEL 5000.0 // Z

#define EN        8       // stepper motor enable, low level effective (note put jumper so automatic)

#define X_DIR     5       // X axis, direction pin
#define Y_DIR     6       // Y
#define Z_DIR     7       // Z

#define X_STP     2       // X axis, step pin
#define Y_STP     3       // Y
#define Z_STP     4       // Z

#define BAUD_RATE 230400  // the rate at which data is read

// AccelStepper is the class we use to run all of the motors in a parallel fashion
// Documentation can be found here: http://www.airspayce.com/mikem/arduino/AccelStepper/classAccelStepper.html
AccelStepper stepper1(AccelStepper::DRIVER, X_STP, X_DIR);
AccelStepper stepper2(AccelStepper::DRIVER, Y_STP, Y_DIR);
AccelStepper stepper3(AccelStepper::DRIVER, Z_STP, Z_DIR);


// Now we declare variables we will use throughout our code (That could change!)
const int ledPin = 13;
// The buffer allows us to store bytes as they are read from the python program (64 bytes in size)
const byte buffSize = 64;
char inputBuffer[buffSize];
// We create inputs to this program by <...> where <> represent the startread and endread markers
const char startMarker = '<';
const char endMarker = '>';

byte bytesRecvd = 0;
boolean readInProgress = false;
boolean newDataFromPC = false;

// WRITE COMMAND: <RUN,DIST,123,F,0.0,0.0,0.0>
// The following is data we will read from the PC. Since the USB reads one byte at a time, we have to store a
// string of bytes in an array called messageFromPC. Then we can grab the relevant information from it.
// Note that in this application, a command sent from python takes the form: <mode, setting, motorID, value, direction, optional>
// Where mode is ["RUN", "SETTING", "JOG", "STOP"]
// setting is string ["ALL"", "FEW", "ONE", "ACCEL", "SPEED", "DELTA"]
// motorID is int [1, 2, 3] (can be combo if numbers ie 123 or 12 or 23)
// value is float [any positive floating number]
// direction is ['F', 'B']
// p1_optional is [any floating number]
// p2_optional is [any floating number]
// p3_optional is [any floating number]

char messageFromPC[buffSize] = {0};
char mode[buffSize] = {0};
int motorID = 0;
int motors[3] = {0,0,0};
AccelStepper steppers[3] = {stepper1, stepper2, stepper3};
char setting[buffSize] = {0};
float value = 0.0;
char dir[buffSize] = {0};
float optional = 0.0;

// These are values that we declare to assign as "settings" to each of the steppers
float motorSpeed = 0.0;
float motorAccel = 0.0;
float oldDistanceLeft1;
float oldDistanceLeft2;
float oldDistanceLeft3;
float jog1Delta;
float jog2Delta;
float jog3Delta;
float toMove;
float p1_toMove;
float p2_toMove;
float p3_toMove;
float p1_optional;
float p2_optional;
float p3_optional;
float distances[3];
signed long p1_distance_to_go;
signed long p1_target_position;
signed long p1_distance_left;

signed long p2_distance_to_go;
signed long p2_target_position;
signed long p2_distance_left;

signed long p3_distance_to_go;
signed long p3_target_position;
signed long p3_distance_left;

signed long distances_to_go[3];
signed long targets_position[3];
signed long distances_left[3];

unsigned long curMillis;
unsigned long prevReplyToPCmillis = 0;
unsigned long replyToPCinterval = 1000;

//=============
// Setup is only called once. When we start up the GUI the Arduino initalizes with a BAUD Rate of _________
void setup() {
  Serial.begin(BAUD_RATE);

  // flash LEDs so we know we are alive
  pinMode(ledPin, OUTPUT);
  digitalWrite(ledPin, HIGH);
  delay(500); // delay() is OK in setup as it only happens once
  digitalWrite(ledPin, LOW);
  delay(500);

  stepper1.setMaxSpeed(X_SPEED);
  stepper2.setMaxSpeed(Y_SPEED);
  stepper3.setMaxSpeed(Z_SPEED);
  // stepper1.setSpeed(X_SPEED);
  // stepper2.setSpeed(Y_SPEED);
  // stepper3.setSpeed(Z_SPEED);
  stepper1.setAcceleration(X_ACCEL);
  stepper2.setAcceleration(Y_ACCEL);
  stepper3.setAcceleration(Z_ACCEL);
  // tell the PC we are ready
  Serial.println("<Arduino is ready>");


}

//=============
// The loop function is what is always running and refreshes BAUD_RATE times per second
void loop() {
  curMillis = millis();
  getDataFromPC();
  // Now is when we determine which mode we are in which dictates which function to call
  //replyToPC();
  //executeThisFunction();
  //replyToPC();
}

//=============
// Here we get data from the serial port, read it one byte at a time, store each subsequent byte in the buffer (list)
// then read it and declare the values to variables in this code
void getDataFromPC() {

  // If there is data from the serial port
  if (Serial.available() > 0) {
    // turn on the LED to indicate we are receiving
    digitalWrite(ledPin, HIGH);
    // read the a single character
    char x = Serial.read();

    // the order of these IF clauses is significant
    if (x == endMarker) {
      readInProgress = false;
      newDataFromPC = true;
      // clear the buffer
      inputBuffer[bytesRecvd] = 0;
      // and parse the data
      return parseData();
    }

    if (readInProgress) {
      // add the character to the buffer
      inputBuffer[bytesRecvd] = x;
      bytesRecvd ++;
      if (bytesRecvd == buffSize) {
        bytesRecvd = buffSize - 1;
      }
    }

    if (x == startMarker) {
      bytesRecvd = 0;
      readInProgress = true;
    }
    digitalWrite(ledPin, LOW);
  }
}


//=============

/*
  # <Mode, Setting, Pump Num, Value>
  # Mode can be SETTING, RUN, JOG, STOP
  # Setting can be SPEED, ACCEL, DELTA, ONE, FEW, ALL, ZERO
  # Pump number can be 1 or 2 or 3 or 12 or 13 or 23. (## indicates two pumps to run)
*/
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

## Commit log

2018-08-29 Added hardware and software release
    [Pump Base v51.stl, Pump Carriage Sled v51.stl, Pump Cover Slide v51.stl, Pump Syringe Brace v51.stl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]
2018-12-03 Fixed multithreading issue. Can currently run multiple motors robustly.
2018-12-14 Fixed typo in arduino code
2019-01-11 Changed the Arduino code for For loops usage and recalibrated
2019-01-12 Steps conversion requires dividing (and multiplying) by microstepping amount, and pitch of screw: 32 and 0.8 respectively
2019-01-14 Revert "Custom flow"
2019-01-16 Update README.MD
    added max flow rates
2019-01-20 Added .STEP and .IGES files for pump and microscope hardware, reorganized HARDWARE folder, and updated the BOM to reflect the most recent one.
    [Pump Base v51.stl, Pump Base.iges, Pump Base.step, Pump Carriage Sled v51.stl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]
2019-01-27 Update README.MD
    max pressure
2019-01-29 Updated BOM with USB microscope
    [poseidon_bill-of-materials_v1.0_2019-01-18.xlsx, poseidon_bill-of-materials_v1.0_2019-01-28.xlsx]
2019-02-01 Added testing data
    [1_poseidon.csv, 2_harvard.csv, 3_harvard.csv, 4_poseidon.csv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]
